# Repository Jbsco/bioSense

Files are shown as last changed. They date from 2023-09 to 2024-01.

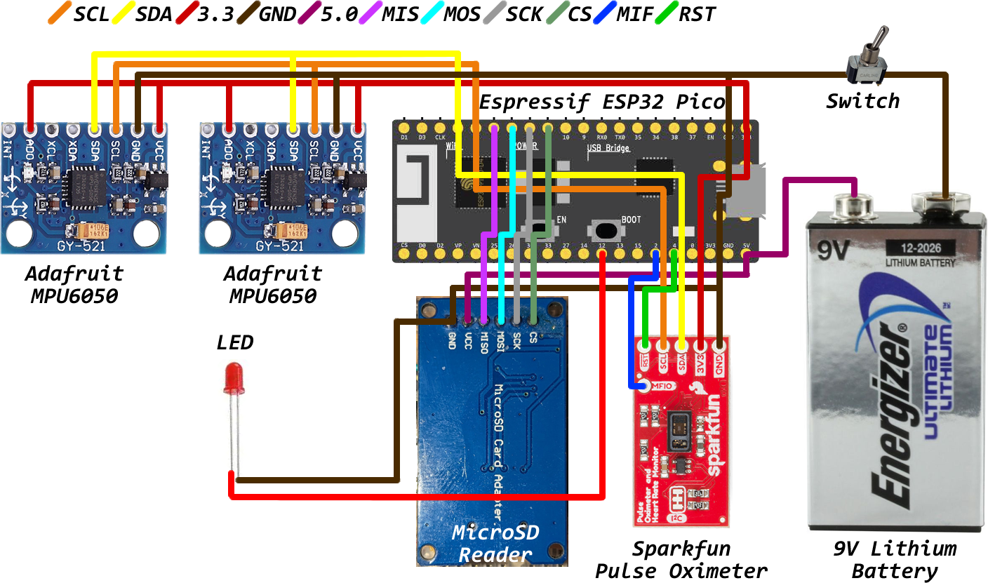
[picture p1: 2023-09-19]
wiring.png

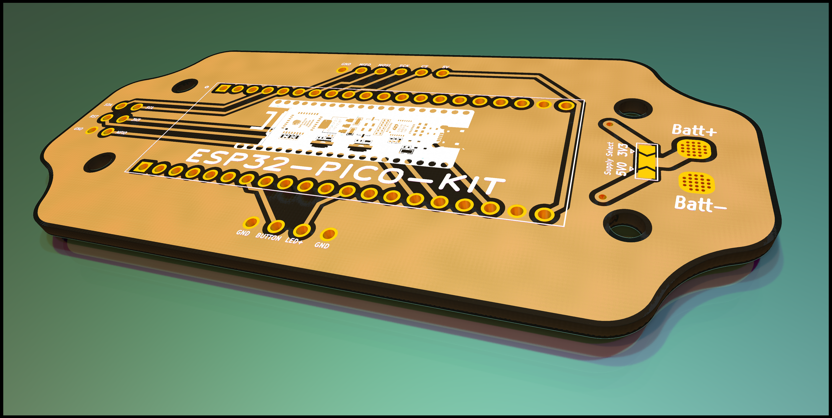
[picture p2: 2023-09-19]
PCB_src/94.5x48.png

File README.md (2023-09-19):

# bioSense

A Spring 2023 project created to assist in ongoing research regarding involuntary breathing movements as exhibited by freedivers performing extended breath holds.

The project was completed and presented at Colorado Mesa University's Spring 2023 Student Showcase and was winner of the Track 4D Design category.

Initially an independent project, the program code was modified and refactored at multiple stages throughout the semester. Hardware functionality was also extended similarly.

See `codeSummary.md` for technical details in the programming of this device.

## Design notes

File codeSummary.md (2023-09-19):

Program Code:
Note that the program code differs from typical Arduino programming in that it utilizes Free-RTOS tasks to make use of
the two available cores on the ESP32-Pico. Free-RTOS is a real-time operating system kernel provided as standard with
Arduino libraries. Using task pinning, functions are able to be assigned to a specific core and will run indefinitely on
that core until the task is cancelled, similar to the typical program loop, which by default only runs on core #1. This
multi-core threading allows grouping of functions that operate across like sensors, such as those using the I2C bus, or
those using the SPI bus. In this specific case, the function `sensorRead` is pinned to core #0, while the function 
`sdWrite` is pinned to core #1. These functions were written such that all I2C bus devices are handled by core #0, while
SPI and analog pin states are handled by core #1. In short, the accelerometer readings and OLED display updates are
handled by one core, and all SD card writes as well as button state and LED pin state are handled by the other. This
breaks up the tasks handled by the microcontroller into two parallel loops that run indefinitely.

Some conflicts can occur with multi-core threading, so care was taken to ensure that no data is written to the same
location by both cores simultaneously. In this case, core #0 only reads accelerometer data, and writes temporary data to
the `fauxList` class where the most recent 10 accelerometer difference samples are stored. Core #1 reads and averages
this data before writing it out to the SD card. Because the accelerometer readings are performed over I2C, and the SD
card writes are performed over SPI, there is no conflict between the two processes.

Both cores are beholden to a state machine with four distinct states. When the microcontroller is powered on,
peripherals are initialized and both threaded tasks are started, each with their own initialization routines before
entering their primary loops. As part of this initialization, `loggingState` (an integer) is set to 0. In this state the
acclerometers and pulse-oximeter sensors are read, averaged, and reported to the OLED display with some graphical
elements. When the button is pressed, the SD card is started and `loggingState` is set to 3, where:
- A correction factor is calculated from the current accelerometer difference to be applied to all data during logging.
- The OLED is set to display a static warning and the correction factor being applied.
- A filename name string is created and formatted with a number that is incremented for each logging session.
- A file with the previous created filename is opened for writing on the SD card.
- Column headers are printed to the file.
- `loggingState` is decremented to 2.
After entering the next state, core #0 will only make sensor reads, and it will do so as quickly as possible. Core #1
will print a character buffer of formatted data at an interval controlled by a flag set by a hardware timer which runs
from `ICACHE RAM`. This interval is able to be specified by setting the `DATAFREQ` define, which is the rate (in Hertz)
that the flag is set. During this state, the OLED is static to allow the sensor reading to happen at maximum speed. When
the button is pressed a second time, `loggingState` is decremented to 1.
In `loggingState` 1, the file is closed, the LED status is turned on, and the correction factor is disabled. After two
seconds, the SD card is unmounted for removal, the LED is turned off, and `loggingState` is decremented to 0 to return
to the initial state.

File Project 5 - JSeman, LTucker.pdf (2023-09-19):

## Differential Measurement

of

## Involuntary Breathing Movements

Jacob Seman
Lillian Tucker

Project 5
EECE244
Spring 2023
Dr. Mellenthin

Table of Contents:

Pg.2 | Overview
Pg.3 | Components
Pg.4 | Wiring Diagram
Pg.4 | PCB Design
Pg.5 | Placement
Pg.5 | Program Code
Pg.7 | Data
Pg.8 | Specifications
Pg.9 | Troubleshooting
Pg.10 Tutorials/References Used Pg.11 Articles and Documents

Overview
A differential measurement was chosen for this project. Two MPU6050 sensors on a wire harness were connected to an ESP32, and readings from the y-axes are compared. The sensors are to be placed at the xiphoid process and on the sternum to detect contractions at the xiphoid and measure them relative to the stable area of the sternum. A custom list class was written to store the MPU sensor data and average it over a defined number of samples, to eliminate measurement noise from the accelerometers. A heart rate and oximeter sensor were also connected to the wire harness. Biometric information is output to an OLED display and states information regarding logging data to the SD card. An access point hosting a web server is created by the ESP32, and a smartphone may be used to connect to the access point and control the remote start & stop of the logging function, as well as the file download and delete function. Selecting “File/Logging Start” mounts the SD card and applies a normalization factor based on the starting conditions (also displayed on the OLED and indicated by an LED) before commencing logging data at 100 Hz. A static message is displayed on the OLED indicating the logging status and correction factor. The LED flashes with each line of buffered data that is written. Selecting “File/Logging Stop” finishes logging and unmounts the SD card for safe removal before continuing to display biometrics. With each logging process, the CSV filename is incremented, so there is no concern about overwriting previous data. The ESP32 has two cores, and threading was used to control the accelerometer and OLED with core #0, while the SD card writing, LED state, and state machine management was controlled by core #1. This allowed reaching a consistent sample rate.

Components
Adafruit MPU6050:
The components used to measure involuntary breathing movements are two Adafruit MPU6050s using an I2C interface. These sensors are attached to the corresponding GND and 3V3 pins of the ESP32 for power. Since these sensors use I2C to communicate, an SCL(serial clock) and SDA(serial data) pin are required to operate. On the ESP32, pin 22 is used for SCL, and pin 21 is used for SDA so the sensors are connected accordingly. The sensors are to be placed at the xiphoid process and on the sternum since most of the movement during involuntary breathing movement occurs in this area.

Sparkfun Pulse Oximeter:
The component used to measure heart rate and blood oxygen levels is an SPO2 sensor that uses an I2C interface. This sensor is placed on the padding of the middle finger on the right hand for optimal reading. This sensor is attached to the corresponding GND and 3V3 pins of the ESP32 for power. Since this sensor uses I2C to communicate, an SCL and SDA pin is required to operate. On the ESP32, pin 22 is used for SCL, and pin 21 is used for SDA so the sensor is connected accordingly.
There is an example library and code that can be downloaded and used to detect heart rate, blood oxygen levels, temperature, and reading status. There are 3 different reading statuses for the SPO2 monitor: 1 means there is no finger detected, 2 means there is a finger detected but isn’t being properly detected, and 3 means there is a finger being properly detected to display heart rate and O2 levels.

OLED Display Screen:
The component used to display heart rate and blood oxygen levels as well as displaying when the system is measuring and logging data is an OLED screen. This component is attached to the corresponding GND and 3V3 pins of the ESP32 for power. Since this component uses I2C to communicate, an SCL and SDA pin is required to operate. On the ESP32, pin 22 is used for SCL and pin 21 is used for SDA so the sensor is connected accordingly.

MicroSD Card Reader:
The component used to log and store the differential data from the accelerometers as well as the oximeter sensor data is a microSD card adapter that uses an SPI interface. This component is attached to the corresponding GND and 5V pins on the ESP32 for power. Since the component uses SPI to communicate, a MISO(master in slave out), MOSI(master out slave in), SCK(serial clock), and CS(chip select/slave select) pin are required to operate. On the ESP32 pin 19 is used for MISO, pin 23 is used for MOSI, pin 18 is used for SCK, and pin 5 is used for CS. A state machine is used for logging data to the microSD card. When using remote start to start logging on the microSD card, a static text is displayed to inform the user it is not safe to dismount the SD card. When using a remote stop to stop logging on the microSD card, a static text is displayed to inform the user when it is safe to dismount the SD card. An LED is used to show when data is being logged onto the microSD card. When data is being written onto the SD card, the LED will turn on. Otherwise, the LED will turn off.

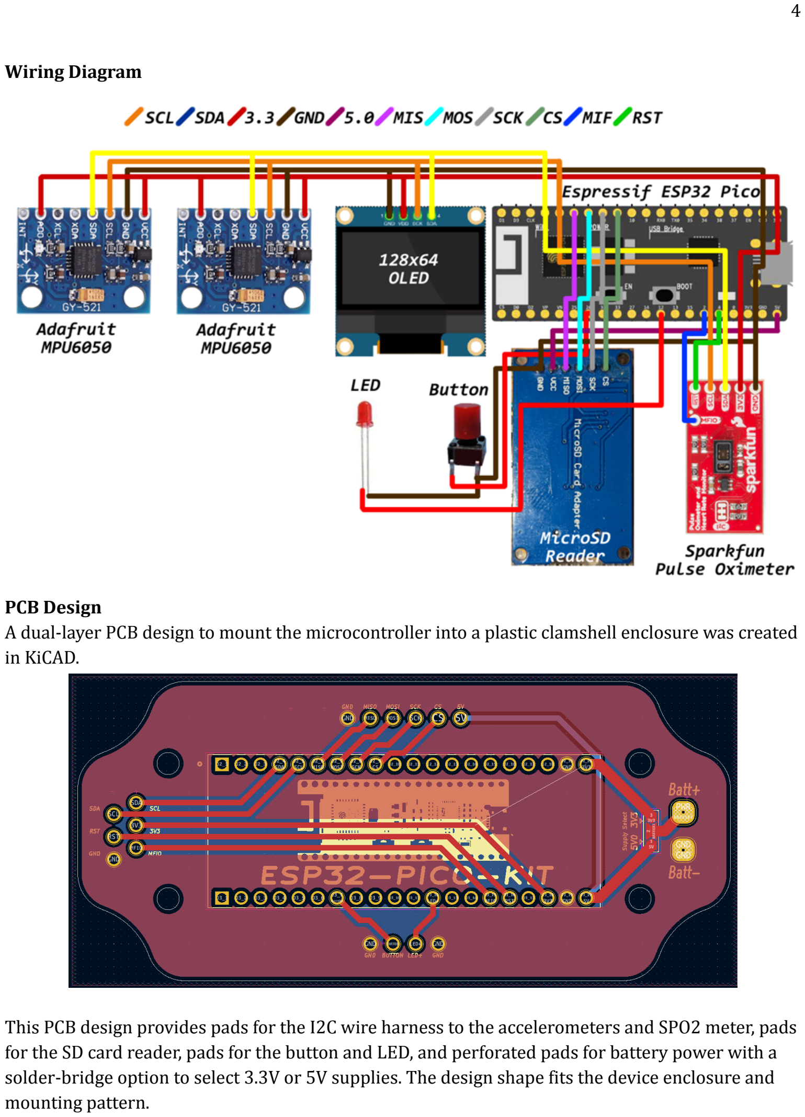
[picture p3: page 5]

Wiring Diagram

PCB Design
A dual-layer PCB design to mount the microcontroller into a plastic clamshell enclosure was created in KiCAD.

This PCB design provides pads for the I2C wire harness to the accelerometers and SPO2 meter, pads for the SD card reader, pads for the button and LED, and perforated pads for battery power with a solder-bridge option to select 3.3V or 5V supplies. The design shape fits the device enclosure and mounting pattern.

Placement
The I2C accelerometers are to be placed with one on the sternum and one over the xiphoid process. The accelerometers may be taped down over clothing provided the clothing is not excessively loose-fitting. The SPO2 sensor may be placed on the pad of a fingertip using tape or the provided velcro strap. To avoid intermittent readings from the SPO2 sensor, it is important to ensure the sensor is not pressing firmly into the pad of the fingertip - very light pressure that keeps the sensor in place without squeezing the fingertip is best. The wire harness is sufficiently long to
accommodate any body shape and size, and may be oriented so that the subject is most comfortable. The microcontroller enclosure is not sensitive to orientation and may be placed nearby the subject rest area however is most convenient.

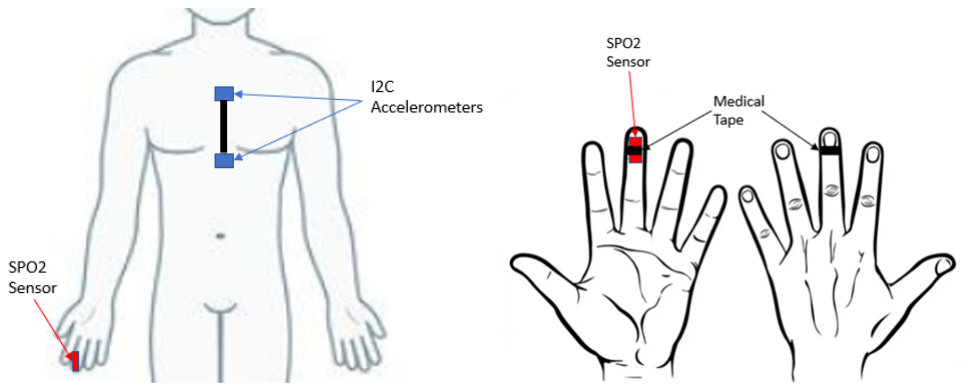
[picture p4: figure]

Program Code

The program code differs from typical Arduino programming in that it utilizes Free-RTOS tasks to make use of the two available cores on the ESP32-Pico. Free-RTOS is a real-time operating system kernel provided as standard with Arduino libraries. Using task pinning, functions are able to be assigned to a specific core and will run indefinitely on that core until the task is canceled, similar to the typical program loop, which by default only runs on core #1. This multi-core “threading” allows the grouping of functions that operate across like sensors, such as those using the I2C bus, or those using the SPI bus. In this specific case, the function “sensorRead” is pinned to core #0, while the function “sdWrite” is pinned to core #1. These functions were written such that all I2C bus devices are handled by core #0, while SPI and analog pin states are handled by core #1. In short, the accelerometer readings and OLED display updates are handled by one core, and all SD card writes as well as button state and LED pin state are handled by the other. This breaks up the tasks handled by the microcontroller into two parallel loops that run indefinitely.

Some conflicts can occur with multi-core threading, so care was taken to ensure that no data is written to the same location by both cores simultaneously. In this case, core #0 only reads accelerometer data, and writes temporary data to the “fauxList” class where the most recent 10 accelerometer difference samples are stored. Core #1 reads and averages this data before writing it

out to the SD card. Because the accelerometer readings are performed over I2C, and the SD card writes are performed over SPI, there is no conflict between the two processes.

Both cores are beholden to a state machine with four distinct states. When the microcontroller is powered on, peripherals are initialized and both threaded tasks are started, each with their own initialization routines before entering their primary loops. As part of this initialization, “loggingState” (an integer) is set to ‘0’. In this state, the accelerometers and pulse-oximeter sensors are read, averaged, and reported to the OLED display with some graphical elements. When the button is pressed, the SD card is started and “loggingState” is set to ‘3’, where:
- A correction factor is calculated from the current accelerometer difference to be applied to all data during logging.
- The OLED is set to display a static warning and the correction factor that is applied.
- A filename name string is created and formatted with a number that is incremented for each logging session.
- A file with the previously created filename is opened for writing on the SD card.
- Column headers are printed to the file.
- “loggingState” is decremented to ‘2’.

After entering the next state, core #0 will only make sensor reads, and it will do so as quickly as possible. Core #1 will print a character buffer of formatted data at an interval controlled by a flag set by a hardware timer that runs from ICACHE RAM. This interval is able to be specified by setting the “DATAFREQ” definition, which is the rate (in Hertz) that the flag is set. During this state, the OLED is static to allow the sensor reading to happen at maximum speed. When the button is pressed a second time, “loggingState” is decremented to ‘1’.

In “loggingState” ‘1’, the file is closed, the LED status is turned on, and the correction factor is disabled. After two seconds, the SD card is unmounted for removal, the LED is turned off, and “loggingState” is decremented to ‘0’ to return to the initial state.

“loggingState” is changed from ‘0’ to ‘3’ anytime the webserver enters the “/loggingst” HTML page, and is changed from ‘2’ to ‘1’ anytime the webserver enters the “/logging” page. These pages are accessed by selecting the “Logging” header tab, and then toggling the “Logging Start/Stop” button.

File download and delete functionality is also available from the web server over WiFi. It is recommended to control the remote start/stop from a smartphone, and to access and download log files seperately from a laptop, although it is possible to download log files from a smartphone if needed. Multiple devices may connect to the microcontroller access point simultaneously, but it is not recommended to start or stop the logging process from anywhere but a single smartphone at a time.

Data
The data may be read by opening the CSV file with MS Excel and creating an XY chart using the data, or by importing the data into Matlab using the provided script. The data is written to the SD card as a CSV file, with a millisecond timestamp in the first column, accelerometer difference in the second column, heart rate in the third column, and oxygen percentage in the fourth column. Normal breathing, a brief breath hold, additional breathing, and then a short, exhaled breath hold are visible in the accelerometer difference plot below. The units for the accelerometer differential
measurement are relative to the sternum and are a measure of the difference magnitude between the two accelerometers. Averaging over 10 samples proved effective at eliminating an appreciable degree of noise from the MPU data.
Output plot showing accelerometer differential measurement (blue), oxygen percentage (orange), and heart rate (red):

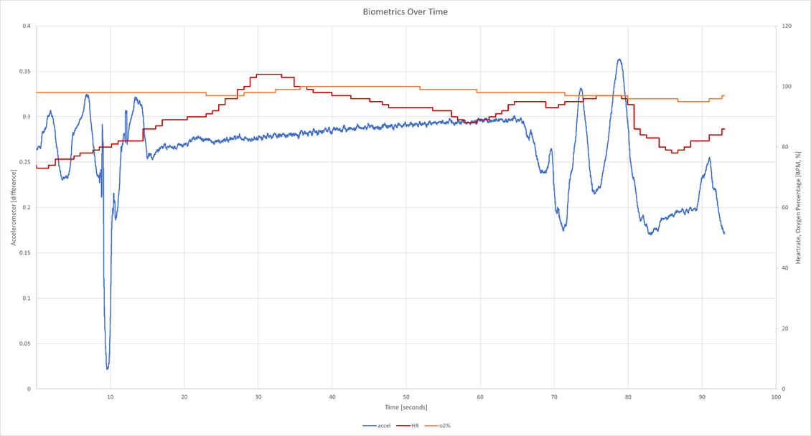
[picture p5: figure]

The data is collected at a 100Hz sample rate, and a MATLAB script to interpret and plot the data is included. The IBM movements are able to be interpreted as a regular oscillation in the “accel_difference” trace, and the beginning of these oscillations marks the onset of the body’s physiological response to extended breath-holding. A scaling factor of x10 is applied to the accelerometer data in MATLAB to align the trace just below the heartrate and oxygen percentage traces.
Postural changes may appear on the accelerometer trace as fluctuations and offsets that do not align with any regular oscillations. Often these posture adjustments result in a new “at-rest” value for the accelerometer difference trace. Most postural adjustments are mitigated or minimized by the differential nature of the measurement, and the fact that the accelerometers are only polled on a single axis. The data is provided with a millisecond timestamp that is converted to seconds by the MATLAB script. This timestamp starts from zero for each logging event.

Specifications

Aspect: | Value:
Power Supply | 5V 2A USB-Micro, Battery
SD Card Format | 5Gb, Fat32
Maximum Sample Rate | ~800Hz
Default Sample Rate | 100Hz (Configurable)
Data Point Averaging | 10 Samples (Default, Configurable)
Data Output | 4 Columns (Incl. Millisecond Timestamp)
Data Format | *.CSV File

Troubleshooting
Oximeter Readings Intermittent/Status Reads 0:
If there is trouble getting a consistent reading from the oximeter sensor, check the placement of the sensor. Ensure the reader is completely covered by the padding of the finger. If readings are still inconsistent, check the pressure on the sensor. If there is too little or too much pressure, reading will not be consistent. Note that readings are usually less consistent when testing on an individual of a darker complexion.

Multi-Threaded I2C Components:
If using multiple I2C components on one set of I2C pins (SDA and SLC), ensure each component has a unique address. This can be done by using the Wire.beginTransmission() function with a unique address in the parenthesis. If each component does not receive a unique address, the components will try to write to the same place.

Cannot Connect to Web Server:
If there is trouble loading/connecting to the web server in your browser:
1. Ensure that the IP address of the web server is correct. The default is “192.168.4.1”.
2. Check that the password used to access the web server is correct. The default is “12345678”.
3. Make sure the libraries and devices are up to date.
4. Check the libraries; There are reports that the libraries including “wifiNINA.h”, “Ethernet”, and “webserver” can be unreliable and incompatible with certain codes and devices.
5. Try using a different browser or different device. The device was found to crash when logging was started from a Windows 10 laptop, but worked consistently without issue when used with an Android smartphone.

Linked below are forums regarding to issues and solutions with connecting and utilizing the web server:
https://www.reddit.com/r/esp32/comments/n5qb2m/esp32_board_seems_to_be_connecting_to_my_network/ (https://www.reddit.com/r/esp32/comments/n5qb2m/esp32_board_seems_to_be_connecting_to_my_network/)
https://github.com/espressif/arduino-esp32/issues/2977https://github.com/espressif/arduino-esp32/pull/7686

Tutorials/References Used
WiFiNina webserver testing -https://docs.arduino.cc/tutorials/uno-wifi-rev2/uno-wifi-r2-hosting-a-webserver

Initial Access Point testing - https://randomnerdtutorials.com/esp32-access-point-ap-web-server/

WiFi Webserver & SD data download - https://www.youtube.com/watch?v=zoYMU1tA3nI Inserted webserver/client functions and CSS stylesheet
Modified HTML to add and support remote start/stop
Removed example file upload functionality
Bug tested, found pending pull request to resolve bug relating to our project (unable to start logging from PC, but works from Android smartphone)

Articles and Documents
Linked below are studies and reports for measuring involuntary breathing movements with prolonged breath holding:
https://www.mdpi.com/2673-7078/2/4/41/pdfhttps://www.ncbi.nlm.nih.gov/pmc/articles/PMC6908740/https://www.tandfonline.com/doi/abs/10.1080/13102818.2010.10817856

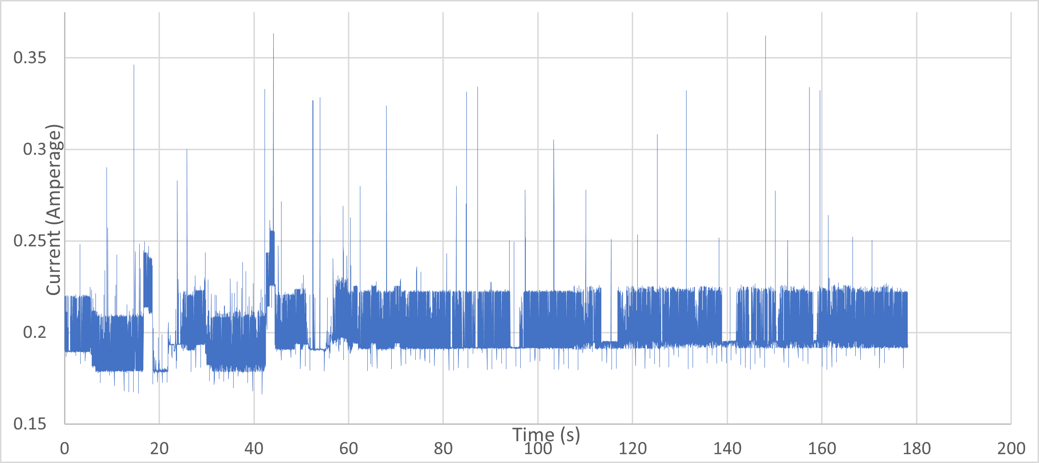
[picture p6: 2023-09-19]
current draw.png

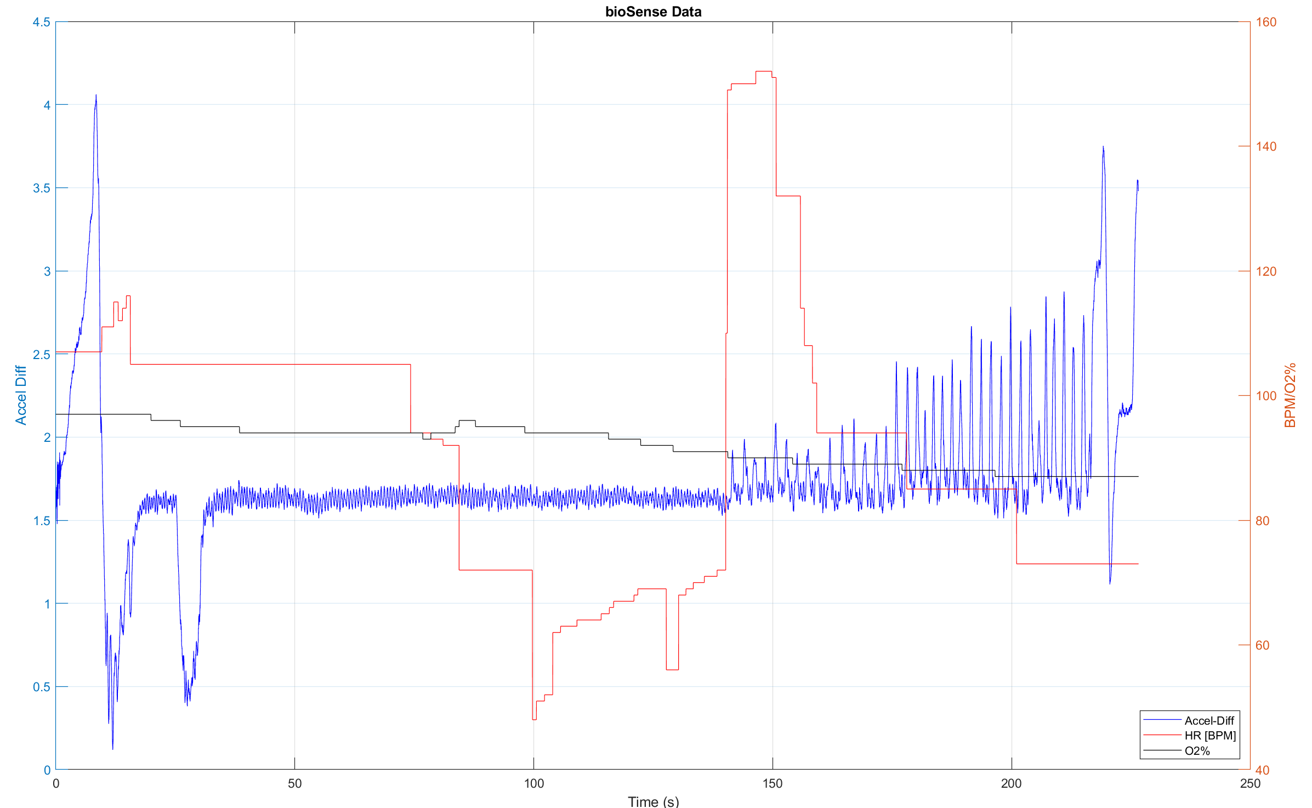
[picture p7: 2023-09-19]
MATLAB_src/data plot.png

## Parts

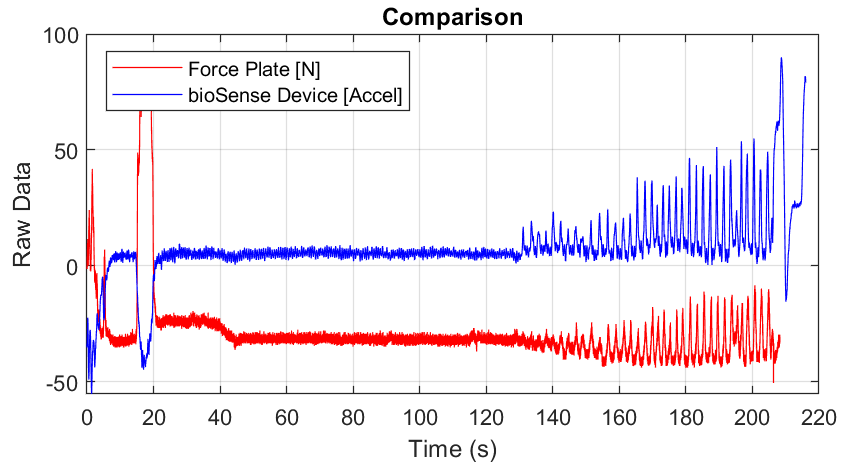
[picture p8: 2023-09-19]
showcase_materials/comparison.png

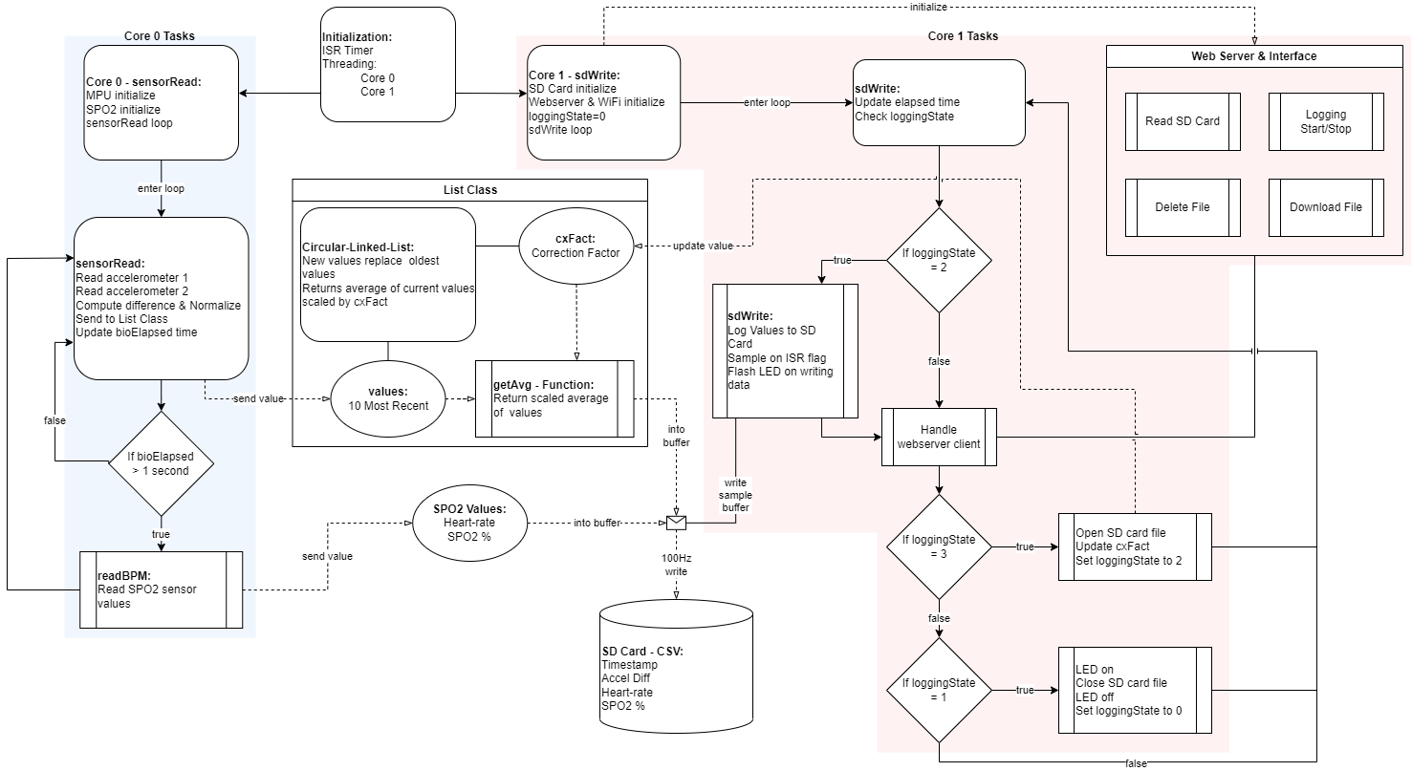
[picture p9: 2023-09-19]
showcase_materials/block.png

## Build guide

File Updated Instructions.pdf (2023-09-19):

QUICKSTART: Microcontroller Usage

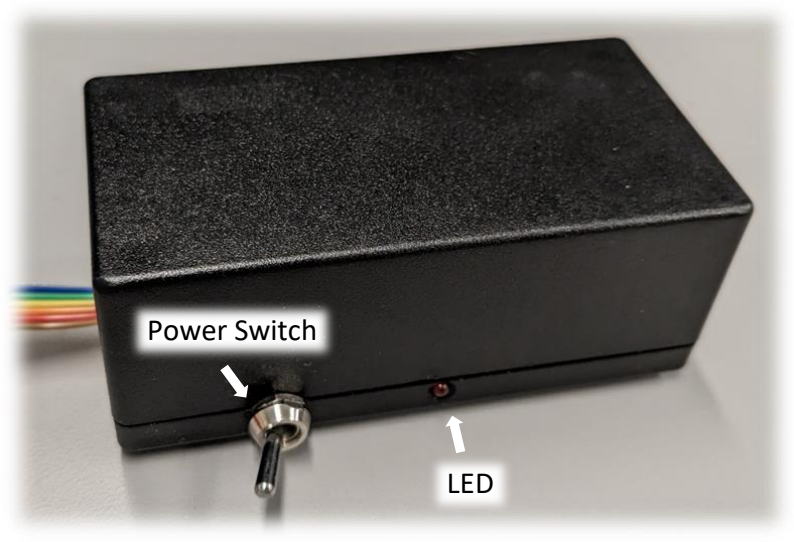
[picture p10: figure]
Power Switch; LED

1. The device is self-powered by a lithium 9V battery. Move the power switch to the on position (toward the LED) to power on.
2. Connect to the “bioSense” WiFi network with the password “12345678”. In a web browser, navigate to the address “192.168.4.1”.
3. Verify sensor placement and subject comfort.
4. When ready to log data, navigate to the “Logging” webserver tab and select “Logging Start”:
a. Data logging will start immediately.
b. Red LED will show active writing activity to SD card.
5. When ready to stop logging data, select “Logging Stop”:
a. SD card will be closed out immediately, and the file will be accessible on the “Files” webserver tab.
b. Another logging session may be started without danger of overwriting the previous log file.
c. Log files are formatted as “data-0001.csv”, “data-0002.csv”, etc.
6. SD card may be re-inserted for continued use without resetting the microcontroller
a. Note that filenames are incremented from “0001” after each microcontroller reset – files may be overwritten if not copied from SD card using an SD card reader and PC before resetting microcontroller and beginning a new logging session
7. Turn the device off when not logging to conserve battery life. Move the power switch away from the LED to power off.
8. If no function is observed, replace the Lithium 9V battery by removing the 4 Phillipshead screws on the enclosure. Only use Lithium replacements to prevent leaking.

QUICKSTART: Sensor Placement

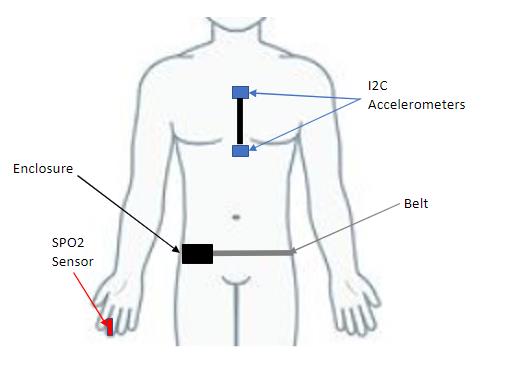
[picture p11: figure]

1. Place accelerometer sensors with one located at the xiphoid process (just below the sternum, in between the rib cage) and the other on the sternum
a. Sensors may be taped in place or secured with elastic
b. Sensors may be placed over clothing provided there are no folds or excessive layers
2. Ensure the sensors are able to move through the range of motion created by a full inhale and exhale without being constricted by the wire harness

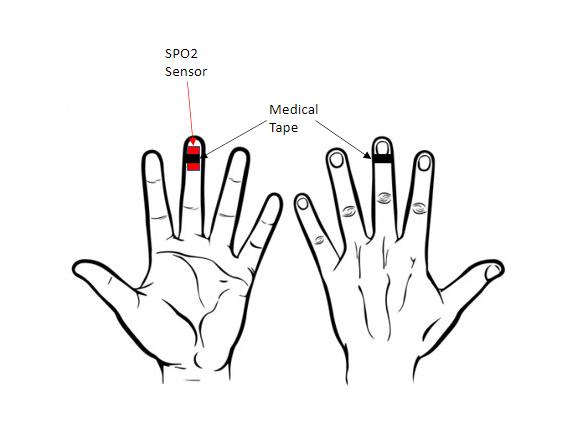
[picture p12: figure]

3. A small Velcro strap is provided to affix the pulse-oximeter to the fore-finger
a. Do not over-tighten when affixing, or readings will be intermittent
b. The sensor should be affixed just firmly enough to stay

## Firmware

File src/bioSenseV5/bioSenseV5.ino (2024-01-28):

/*          ____   ____  ___        _____   ___  ____    _____   ___ 
           |    \ |    |/   \      / ___/  /  _]|    \  / ___/  /  _]
           |  o  ) |  ||     |    (   \_  /  [_ |  _  |(   \_  /  [_ 
           |     | |  ||  O  |     \__  ||    _]|  |  | \__  ||    _]
           |  O  | |  ||     |     /  \ ||   [_ |  |  | /  \ ||   [_ 
           |     | |  ||     |     \    ||     ||  |  | \    ||     |
           |_____||____|\___/       \___||_____||__|__|  \___||_____|V5

/ / / / / / / / / / EECE244 Applications of Embedded Systems \ \ \ \ \ \ \ \ \ \
/ / / / /  Written by Jacob Seman & Lillian Tucker for the ESP32 Pico  \ \ \ \ \
                                   March 2023
                                 Functionality:
                        WiFi Access Point Implementation
           Read differential MPU data to detect involuntary contractions
                     Measure heartrate and oxygen percentage
                         Log data to SD card at 100Hz
                        Indicate read/write status LED
                      Webserver interface to start/stop
                     Utilize threading and hardware timers
\ \ \ \ \ \ \ \ \ \ \ \  NOTE: DO NOT RUN FROM USB HUB / / / / / / / / / / / / /
\ \ \ \ \ \ \ \ \ THE ESP32 WILL BROWNOUT ON LOW QUALITY HUBS  / / / / / / / /*/

#include <Adafruit_SSD1306.h>
#include <Adafruit_Sensor.h>
#include <SparkFun_Bio_Sensor_Hub_Library.h>
#include <Wire.h>
#include <WiFi.h>
#include <ESP32WebServer.h>
#include <ESPmDNS.h>
#include "CSS.h"
#include "FS.h"
#include "SD.h"
#include "SPI.h"
#include "esp_task_wdt.h" // to configure core tasks' watchdogs
#include "esp_timer.h"

#define DEF_ADDR 0x55
#define AVG_AMT  10
#define RESETPIN 4
#define MFIOPIN  2
#define DATAFREQ 100 // [Hz] modify here for data rate, 100Hz default
#define ISRSPEED 1000 // [1/seconds] timer divider, millis by default
#define servername "bioSense"

/* FAUXLIST: vector class is not defined for Arduino:
    - not all functions of vector type are needed here.
    - simple custom class works for now
    - this functions similarly to a list,
      by updating 'pos' and overwriting old values.
      this saves on time spent in loops while in data collection state.      */
class fauxList{
  float vals[AVG_AMT];
  int pos;
  public:
    // this factor should be updated at logging start:
      // used to scale logging data to 1.0 from the initial value
    float cxFact;
    fauxList(){
      for(int i=0;i<AVG_AMT;i++)vals[i]=0;
      pos=0;
      cxFact=1.0;
    }
    void pushback(float newVal){ // push to 'pos' in list
      vals[pos]=newVal; // replace next 'pos', it will always be oldest in list
      pos++; // update 'pos' in FIFO scheme, roll through whole list
      if(pos>=AVG_AMT)pos=0; // reset at end of cycle
    }
    float getAvg(){ // now only calculated on request and not every pushback
      float avg=0;
      for(int i=0;i<AVG_AMT;i++){ // get avg
        avg+=fabs(vals[i]);
      }
      avg/=AVG_AMT;
      avg*=cxFact;
      return avg;
    }
};

/* PROTOTYPES:*/
void initMPU();
float getAccelDiff();
void initDisplay();
void initSPO();
void initSD();
void initTimer();
void ICACHE_RAM_ATTR onTimerISR();
/* ONTIMERISR: hardware interrupt to set takeSample flag on data rate interval:
    - could alternatively look into micros() or microsISR() from "time.h"
      but running this function from RAM allows some addtional event control
    - overall logging state cycle time for all processes is fast anough to hit
      ~800Hz. when set for 1kHz, the cycle is usually 1ms, but longer when
      bioData reads occur, up to 9ms.
    - data resolution is likely sufficient at 100Hz, and when configured for
      this rate the ESP32 is able to consistently hit 10ms cycle times
      (plus/minus only 1ms), and this is corrected by retaining interval
      overruns in the ISRcount calculation.                                   */
void initThreading(); // start threads
/* INITTHREADING: threading is used to take advantage of the ESP32's two cores:
    - this allows splitting function calls between core #0 and #1, to reach 1kHz
    - note that the I2C bus should only be accessed by a single core
      and not both cores independently
    - else thread-unsafe behavior occurs,
      mainly corruption of the content pushed to the OLED display
    - this means that whatever core reads the MPU6050 sensors
      must also run the OLED display functions                                */
void sensorRead(void *param); // assigned to core #0
void sdWrite(void *param); // assigned to core #1
void handleFileUpload();
//void runFunc(); // function under test
//void measure_function(); // timing FUT for 5000 iterations

/* GLOBALVARIABLES:*/
int16_t acc1,acc2; // containers for accelerometer readings
uint8_t takeSample,loggingState; // flag set on DATAFREQ interval, logging state
uint fileNum,sampleRateMillis; // filename session number, etc.
ulong elapsedTime,previousTime,bioElapsed,bioPrevious,
      isrCount,isrElapsed,isrPrevious;
char nameBuffer[21],dataBuffer[29],countBuffer[3]; // buffers for snprintf
hw_timer_t *timer=NULL; // ISR timer
TaskHandle_t core0,core1; // threading handlers
fauxList accelArray; // averaging fauxList, reduces noise
File dataFile; // SD card file
Adafruit_SSD1306 display=Adafruit_SSD1306(128,32,&Wire); // OLED
SparkFun_Bio_Sensor_Hub bioHub(RESETPIN,MFIOPIN); // pulse oximeter
bioData body; // pulseox container

/*IPAddress local_ip(192,168,4,1);
IPAddress gateway(192,168,4,1);
IPAddress subnet(255,255,255,0);*/
ESP32WebServer server(80);

/* SETUP:*/
void setup(){
  Serial.begin(115200);
  setCpuFrequencyMhz(240); // maximum safe (default) CPU speed
  Serial.print("CPU freq set to ");
  Serial.print(getCpuFrequencyMhz());
  Serial.println(" MHz");
  Serial.print("setup() is running on core ");
  Serial.println(xPortGetCoreID());
  pinMode(26,INPUT_PULLUP); // init button
  pinMode(12,OUTPUT); // init write LED
  initTimer(); // begin ISR timer
  initThreading(); // begin threaded tasks
}

void loop(){} // not sure if arduino, or real-time operating system...unused.

/* INITMPU:*/
void initMPU(){
  Wire.begin(); // Initialize comunication
  Wire.setClock(400000L);
  Wire.beginTransmission(0x68); // Start communication with MPU6050 // MPU=0x68
  Wire.write(0x6B); // Talk to the register 6B
  Wire.write(0x00); // Make reset - place a 0 into the 6B register
  Wire.endTransmission(true); //end the transmission
  Wire.beginTransmission(0x69); // Start communication with MPU6050 // MPU=0x69
  Wire.write(0x6B); // Talk to the register 6B
  Wire.write(0x00); // Make reset - place a 0 into the 6B register
  Wire.endTransmission(true); //end the transmission
}

/* GETACCELDIFF: only read the y-axes from both MPUs, and store difference*/
float getAccelDiff(){
  Wire.beginTransmission(0x68);
  Wire.write(0x3D); // Start with register 0x3D (ACCEL_YOUT_H)
  Wire.endTransmission(false);
  Wire.requestFrom((uint8_t)0x68,(uint8_t)2,(uint8_t)true); // Read 2 registers
    // ***typecasting required to reduce compiler overload candidate guessing
  acc1=(Wire.read()<<8|Wire.read()); // Y-axis value from mpu1
  Wire.beginTransmission(0x69);
  Wire.write(0x3D); // Start with register 0x3D (ACCEL_YOUT_H)
  Wire.endTransmission(false);
  Wire.requestFrom((uint8_t)0x69,(uint8_t)2,(uint8_t)true); // Read 2 registers
    // ***typecasting required to reduce compiler overload candidate guessing
  acc2=(Wire.read()<<8|Wire.read()); // Y-axis value from mpu2
  return (acc2-acc1)/16384.0; // LSB/g
}

/* INITDISPLAY:*/
void initDisplay(){
  if (!display.begin(SSD1306_SWITCHCAPVCC,0x3C)) { // address 0x3C for OLED
    Serial.println("SSD1306 init failed");
    while(1)yield();
  }
  Serial.println("SSD1306 init complete");
  display.display();
  delay(500); // pause for 0.5 seconds to catch up
  display.setTextSize(1);
  display.setTextColor(WHITE);
  display.setRotation(0);
  display.clearDisplay();
  display.display();
}

/* INITSPO:*/
void initSPO(){
  Wire.begin();
  int result=bioHub.begin();
  if(!result)Serial.println("biosensor init started...");
  else Serial.println("could not communicate with the sensor.");
  Serial.println("configuring biosensor...");
  int error=bioHub.configBpm(MODE_TWO); // Configuring BPM settings
  if(!error)Serial.println("biosensor configured.");
  else{
    Serial.println("error configuring sensor.");
    Serial.print("error: ");
    Serial.println(error);
  }
  delay(2000); // pause for 2 seconds to catch up
}

/* INITSD:*/
void initSD(){
  // SD card setup:
  Serial.println("initializing SD card...");
  if (!SD.begin(SS)){
    Serial.println("initialization failed.");
    while(1);
  }else Serial.println("SD init complete, card present");
   // print the type of card:
  Serial.print("card type: ");
  switch (SD.cardType()){
    case CARD_NONE:
      Serial.println("NONE");
      break;
    case CARD_MMC:
      Serial.println("MMC");
      break;
    case CARD_SD:
      Serial.println("SD");
      break;
    case CARD_SDHC:
      Serial.println("SDHC");
      break;
    default:
      Serial.println("Unknown");
  }
  // print the size of the first FAT-type volume:
  Serial.print("Card size: ");
  Serial.println((float)SD.cardSize()/1000);
  Serial.print("Total bytes: ");
  Serial.println(SD.totalBytes());
  Serial.print("Used bytes: ");
  Serial.println(SD.usedBytes());
  loggingState=0; // set state
  fileNum=0; // set data log file number
  //SD.end();
}

/* INITTIMER: set hardware clock division to be used by ISR*/
void initTimer(){
  sampleRateMillis=ISRSPEED/DATAFREQ;
  takeSample=0;
  isrCount=0;
	timer=timerBegin(0,20,true);
	timerAttachInterrupt(timer,&onTimerISR,true);
	timerAlarmWrite(timer,4000000/ISRSPEED,true); // 4MHz clock div data-frequency
  timerAlarmEnable(timer);
  Serial.print("ISR timer initialized at ");
  Serial.print(ISRSPEED);
  Serial.println(" Hz.");
}

/* ONTIMERISR: timer sets the flag at sample rate by clock division count*/
void ICACHE_RAM_ATTR onTimerISR(){
  isrCount++;
  isrElapsed=isrCount-isrPrevious;
  if(isrElapsed>=sampleRateMillis&&!takeSample){
    takeSample=1;
    // correction for millisecond losses over time:
    isrPrevious=isrCount;//-(isrElapsed-sampleRateMillis);
  }
}

/* INITTHREADING: pin functions to cores, run two loops in parallel*/
void initThreading(){
  // core 0, 10kbyte stack:
  xTaskCreatePinnedToCore(sensorRead,"sensorRead",10000,NULL,1,&core0,0);
  // core 1, 10kbyte stack:
  xTaskCreatePinnedToCore(sdWrite,"sdWrite",10000,NULL,1,&core1,1);
}
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
